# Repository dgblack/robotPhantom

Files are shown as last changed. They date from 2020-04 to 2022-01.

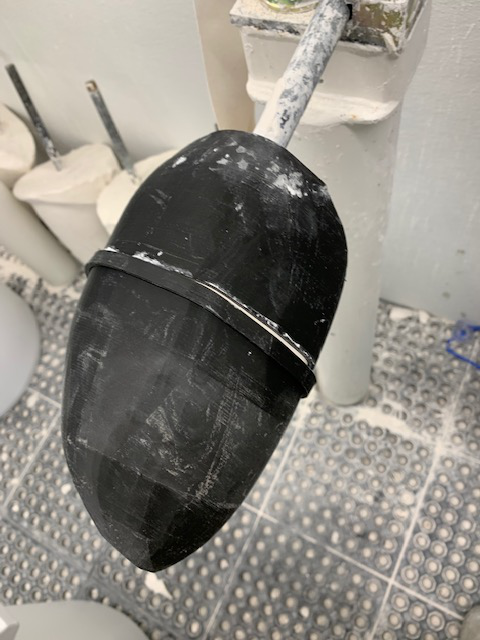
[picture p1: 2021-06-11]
Photos:Videos/image01.jpeg

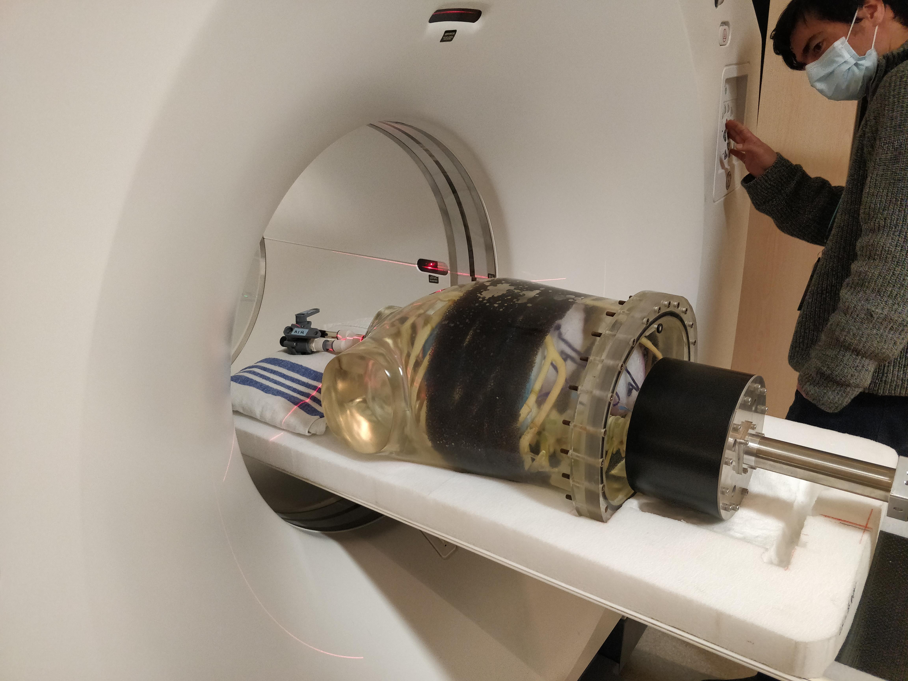
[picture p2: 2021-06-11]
Photos:Videos/IMG_20210426_1102451.jpg

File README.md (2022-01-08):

# Robotic PET Phantom

### Authors:
- David Black  (Engineering Physics, University of British Columbia, Vancouver, Canada)
- Yas Oloumi Yazdi (Engineering Physics, University of British Columbia, Vancouver, Canada)
- Jeremy Wong (Engineering Physics, University of British Columbia, Vancouver, Canada)
- Ivan Klyuzhin (BC Cancer Research Centre, Vancouver, Canada)

### Overview:
Full mechanical, electrical, and software design of an anatomically realistic, anthropomorphic PET phantom with human-like breathing motion. The phantom is robust and can achieve fast breathing rates (over 25 breaths per minute) even at high tidal volumes (up to 1000mL). The lungs have not yet been fabricated due to the COVID-19 pandemic.

### Videos and Photos:
See demo video [here](https://youtu.be/zXkUx0RQXnE)  
Some videos and photos from testing [here](https://ubcca-my.sharepoint.com/:f:/g/personal/dgblack_student_ubc_ca/Ejtq5QNHxeNPp8weYnc7cZwBMOwxvVZQ7KxTPI8Fzo8WOQ)

### Paper:
To read about the phantom, read the Medical Physics paper about it [here](https://github.com/dgblack/robotPhantom/blob/3cfdd82dce6134d97d138fe47dd0202dabd2ce38/MedicalPhysicsPaper.pdf)\
See ePoster [here](https://w3.aapm.org/meetings/2020AM/programInfo/programAbs.php?sid=8796&aid=51718)

### User Manual:
For full details, documentation, user manual, click [here](https://github.com/dgblack/robotPhantom/blob/master/phantomUserManual.pdf)

### Bill Of Materials:
View the BOM [here](https://docs.google.com/spreadsheets/d/1NjVN7iGE2hLrNtNaS808veyB4rukoj4t-0Kp28Ju0Y0/edit?usp=sharing)\
Or download a PDF version [here](https://github.com/dgblack/robotPhantom/raw/master/BillOfMaterials.pdf)

### CAD Models 
(Plus machine shop drawings, DXF files for waterjetting, STL files for 3D printing)\
View files [here](https://github.com/dgblack/robotPhantom/tree/master/CAD)

### Software
Code is found [here](https://github.com/dgblack/robotPhantom/tree/master/src)

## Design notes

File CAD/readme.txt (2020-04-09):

The CAD files are named by part number, which can be referenced from the Bill Of Materials. Certain DXF files for waterjet cutting, drawings for machine shops, and STL files for 3D printing are included in the Fabrication folder. While these are easily reproduced by exporting from SolidWorks, they are the files we used for fabrication.

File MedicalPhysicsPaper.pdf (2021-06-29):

## Design of an anthropomorphic PET phantom with elastic lungs and respiration modeling

David G. Black, Yas Oloumi Yazdi and Jeremy Wong
Department of Physics and Astronomy, University of British Columbia, Vancouver, BC, Canada
Roberto Fedrigo
Department of Physics and Astronomy, University of British Columbia, Vancouver, BC, Canada BC Cancer Research Institute, Vancouver, BC, Canada
Carlos Uribe
Department of Functional Imaging, BC Cancer, Vancouver, BC, Canada
Department of Radiology, University of British Columbia, Vancouver, BC, Canada
Dan J. Kadrmas
Department of Radiology and Imaging Sciences, University of Utah, Salt Lake City, UT, USA
Arman Rahmima)
Department of Physics and Astronomy, University of British Columbia, Vancouver, BC, Canada BC Cancer Research Institute, Vancouver, BC, Canada
Department of Radiology, University of British Columbia, Vancouver, BC, Canada
Ivan S. Klyuzhin
BC Cancer Research Institute, Vancouver, BC, Canada
Department of Radiology, University of British Columbia, Vancouver, BC, Canada
(Received 27 December 2020; revised 6 May 2021; accepted for publication 10 May 2021; published xx xxxx xxxx)
Purpose: Respiratory motion during positron emission tomography (PET) scans can be a major detriment to image quality in oncological imaging. The impact of motion on lesion quantification and detectability can be assessed using phantoms with realistic anatomy representation and motion modeling. In this work, we develop an anthropomorphic phantom for PET imaging that combines anatomic fidelity and a realistic breathing mechanism with deformable lungs.
Methods: We start from a previously developed anatomically accurate but static phantom of a human torso, and add elastic lungs with a highly controllable actuation mechanism which replicates the physics of breathing. The space outside the lungs is filled with a radioactive water solution. To maintain anatomical accuracy and realistic gamma ray attenuation in the torso, all motion mechanisms and actuators are positioned outside of the phantom compartment. The actuation mechanism can produce custom respiratory waveforms with breathing rates up to 25 breaths per minute and tidal volumes up to 1200 mL. Results: Several tests were performed to validate the performance of the phantom assembly, in which the phantom was filled with water and given respiratory waveforms to execute. All parts demonstrated expected performance. Force requirements were not exceeded and no leaks were detected, although continued use of the phantom is required to evaluate wear. The motion of the lungs was determined to be within a reasonable realistic range.
Conclusions: The full mechanical design is described in this paper, as well as a software application with graphical user interface which was developed to plan and visualize respiratory patterns. Both are available online as open source files. The developed phantom will facilitate future work in evaluating the impact of respiratory motion on lesion quantification and detectability in clinical practice. © 2021 American Association of Physicists in Medicine [https://doi.org/10.1002/mp.14998]

Key words: anthropomorphic phantom, motion correction, motion management, pet, phantoms -physical, quantitative imaging/analysis

1. INTRODUCTION

Positron emission tomography (PET) imaging is widely used in oncology for tumor detection, monitoring, and quantification. A leading factor that can adversely affect the quality of thoracic PET images is respiratory motion during the scans.¹ In normal respiration, the amplitude of diaphragm movement is on the order of 1.5–2 cm,² while deep inspiration may result in 7–13 cm diaphragm displacement.³ For clinical PET scanners with spatial resolution around 0.4–0.5 cm fullwidth at half-maximum (FWHM), motion of this magnitude can lead to effective resolution closer to 1 cm.⁴,5 This can reduce contrast for small lesions (e.g. cancer metastases⁶ ),
worsen lesion detectability, and introduce bias in the measured standardized uptake values (SUVs). In some cases, the measured values of functional metrics such as mean and
1 | Med. Phys. 0 (0), xxxx | 0094-2405/xxxx/0(0)/1/xx | © 2021 American Association of Physicists in Medicine | 1

maximum SUV (SUVmean, SUVmax) can directly affect therapy planning and post-treatment outcome analysis.⁷,8 For larger lesions, respiratory motion may likewise introduce bias in radiomic features that quantify lesion shape and texture.⁹⁻ 11 Additionally, the mismatch between PET and computed tomography (CT) images due to motion may lead to errors in attenuation correction and scatter estimation.¹²,13
Hence, there is an extensive ongoing effort to understand and evaluate the effect of respiratory motion in routine clinical PET imaging, particularly with respect to thoracic lesion detectability and quantification.¹⁴⁻¹⁶ For a quantitative assessment of such effects, it is necessary to obtain the ground truth activity values of lesions without respiration. In human subjects, respiratory gating and/or breath hold techniques can be used to reduce the effects of respiratory motion to obtain in vivo proxy measures of ground truth lesion activities, but these techniques are imperfect, subject to increased noise, and may be challenging in practice.¹⁷ In contrast, physical phantoms with various levels of complexity and realism offer a powerful experimental approach where the ground truth activity is precisely known. One of the most common approaches is to mount a rigid torso phantom on an actuated platform that can generate translational motion with a precisely known trajectory, such as the QUASAR system (Modus QA, Ontario, Canada). For example, such an approach was used by Liu et al.,¹⁸ who reported underestimation of SUVmax by 28% for 1 cm lesions due to motion. In another study that used a similar approach, contrast recovery for hot spheres in a phantom was found to be reduced by nearly 50% due to motion.¹⁹ With continuing advances in PET scanner sensitivity and resolution,²⁰ as well as development of novel image quantification paradigms,²¹ it becomes of interest to evaluate the effects of respiratory motion under more anatomically realistic conditions. Rigidly moving thorax phantoms, no matter how geometrically realistic, do not simulate several important effects of respiratory motion, namely motion of organs and lesions with respect to the ribcage, or changes in attenuation due to lung volume change. In order to simulate such effects, relative movement of internal compartments inside the phantom must be implemented. The goal of this work was to develop an anthropomorphic phantom for PET imaging, which combines anatomic fidelity and a realistic breathing mechanism with deformable lungs. We propose and test an approach wherein elastic lungs are manufactured from 3D-printed molds, and actuation is performed by means of creating a negative pressure differential inside the thorax – similar to how real breathing occurs in humans. We build upon an existing phantom previously developed by Kadrmas et al.,²²,23 henceforth referred to as “Probe-IQ” (Image Quality Probe), which has previously been static and not used to study motion effects. To the best of our knowledge, Probe-IQ to this day has the highest level of anatomical realism in the field. In the development of the motion-enabled phantom and lung actuation mechanism described in this paper, we use the shell and rib-cage of the original Probe-IQ phantom, but add custom-built elastic lungs with trachea, and an electronically controlled linear actuator to drive the lung deformation. The phantom is intended for use in PET imaging to evaluate the effect of respiratory motion on lesion quantification.
Several other anthropomorphic phantoms with focus on respiratory motion modeling in PET/CT imaging have been developed in the past; they are listed in Table I in comparison to the motion-enabled Probe-IQ. While Wilhelm²⁴ has the most realistic overall motion of any existing device, it lacks any bone structure, which is important for accurately modeling the gamma ray attenuation and scatter. Conversely, Alderson²⁵ has bones as well as respiratory and cardiac motion; however, its anatomy is simplified and it does not support the addition of lesions. Besides PET/CT imaging, several anthropomorphic phantoms have been developed specifically for radiation dosimetry and radiotherapy planning.²⁶,27 In such phantoms lungs are typically inflated using a ventilator that applies positive air pressure.²⁸⁻³⁰ However, driving lungs by ventilation is difficult when they are surrounded by an incompressible medium, for example, a radioactive water solution. In contrast, our approach is based on a more realistic principle of creating a negative pressure differential inside the thorax, forcing the lungs to inflate; the advantages of this approach are described later in the manuscript.
In this paper, we carefully consider the technical challenges associated with the proposed phantom design, and describe the functional requirements. To facilitate the re-use of our work by other groups, the implementation of the phantom is described in detail, including open-sourced schematics, materials, and software. Finally, we test the function of the completed phantom assembly and perform CT scans with artificial lung lesion tracking to validate the proposed method of lung actuation.
2. MATERIALS AND METHODS
2.A. Design overview
The Probe-IQ phantom enhanced with respiratory motion capabilities aims to achieve the following:
- Anatomical accuracy
- Builds off the static anatomical accuracy of Probe-IQ and achieves realistic lung motion.
- Avoids any unrealistic parts like connecting rods or metal components in the torso.

TABLE I. Comparison of existing anthropomorphic phantoms of interest.

Name

PET/CT/
MRI CM RM LM SS Lesions

Probe-IQ + Respiratory
motion capabilities
| ✓/ ✓/ × | × | ✓ | ✓ | ✓ | ✓
Probe-IQ²²,23 | ✓/ ✓/ × | × | × | × | ✓ | ✓
Wilhelm²⁴ | ✓/ ✓/ ✓ | ✓ | ✓ | ✓ | × | ✓
Alderson²⁵ | ✓/ ✓/ × | ✓ | ✓ | × | ✓ | ×

CM, cardiac motion; RM, respiratory motion; LM, liver motion; SS, skeletal structure.

Medical Physics, 0 (0), xxxx

2 | Black et al.: Anthropomorphic respiratory PET phantom | 2

- All materials carefully selected with reference to mass attenuation coefficients³¹ or tests²⁴ to resemble human tissue.
- Respiratory motion control
- Able to achieve a wide range of breathing rates and tidal volumes (i.e. air displaced between inhalation and exhalation). Namely, at least up to 25 breaths per minute at 1 L tidal volume; typical relaxed breathing is 500 mL tidal volume at 15–20 breaths per minute.³²
- Has highly controllable, repeatable, consistent breathing motion to generate high quality data, but also can include occasional disrupted breaths or inconsistencies, as would happen in a real patient.
- Realistic actuation principle.

In addition, safety is a concern, as the phantom is filled with approximately 15 L of radioactive solution (300 to 1000 MBq of radioactivity per scan) for PET acquisitions. The design must avoid leaks, and minimize the possibility of large spills. Easy fill-ability of the phantom is also desirable to reduce radiation exposure to users and to increase usability.
The respiratory motion-enabled Probe-IQ phantom involves three main components: (a) elastic and realistically shaped lungs, (b) an actuation method, and (c) a control system (electronics and software). The overall structure can be seen in Fig. 1 and all design files and code can be accessed in the Open Source Section at the end of this paper. The lungs are located inside the rib cage of the existing Probe-IQ phantom (A), and surrounded by a radioactive water solution creating the nonspecific radioactivity background typically present in oncological PET images. The lungs are connected to the atmosphere by a breathing tube (trachea) (F), which can be sealed at the neck. The actuating mechanism is positioned below the phantom (B, C, D), where the pelvis of a human would be located. It is outside the field of view of the PET scanner with a standard axial extent, so as not to create image artifacts. The phantom operates by piston-actuated passive breathing, as explained below and seen in Fig. 2.
To achieve respiratory motion with the lungs, the mechanism modulates the volume or pressure of the whole phantom in a manner analogous to real human breathing. Since the phantom is sealed, rigid, and entirely filled with water, except for the air-filled lungs, changing its volume by ΔV induces an equal volume change of ΔV in the lungs. Instead of compressing the air in a sealed set of lungs, the pressure requirement of the actuating mechanism can be dramatically decreased by opening the lungs to the atmosphere once the phantom has been filled and sealed. Contrary with intuition, the lungs do not collapse under the pressure of the water since the water volume is constant and cannot expand to fill the vacant space created if the lungs were to collapse. In effect, a relative negative pressure is created in the liquid anterior to the lungs, just as human breathing relies on negative intrapleural pressure. Now, when the volume of the torso is changed, that volume of air is simply exhaled to or inhaled from the atmosphere (Fig. 2).
To prepare the phantom for imaging, the lungs, organs, and bones are positioned inside the thorax, and the lungs are pressurized using a Schrader valve (Fig. 3) before completely filling the phantom with radioactive water solution. A valve in the base plate, at the highest point in the torso, is used to release the displaced air (Fig. 3). Once the phantom is filled and sealed, the lungs are opened to the atmosphere.
With the phantom setup, the user can define custom respiratory patterns, rates, and volumes using a graphical user interface. The piston then moves along the defined trajectory for the duration of a scan, causing the lungs to expand and contract. The next three sections describe the lungs, breathing mechanism, and software in more detail.

2.B. Lungs
The lung shapes were derived from a CT scan of an adult male and simplified using mesh editing software (Blender Foundation, Amsterdam) to reduce the cardiac notch and

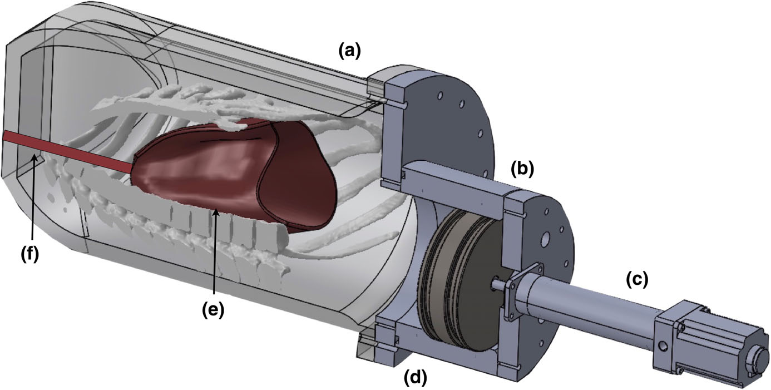
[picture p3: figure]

FIG. 1. Overview of phantom design. A: existing thorax shell and bone structure (liver and heart compartments included but not pictured). B: Piston and cylinder for torso volume modulation. C: linear actuator. D: custom-designed base-plate allows compatibility with existing Probe-IQ phantom. E: flexible lung inserts of silicone elastomer. F: breathing tubes (trachea) connect lungs to atmosphere to allow air transfer during inhalation and exhalation.

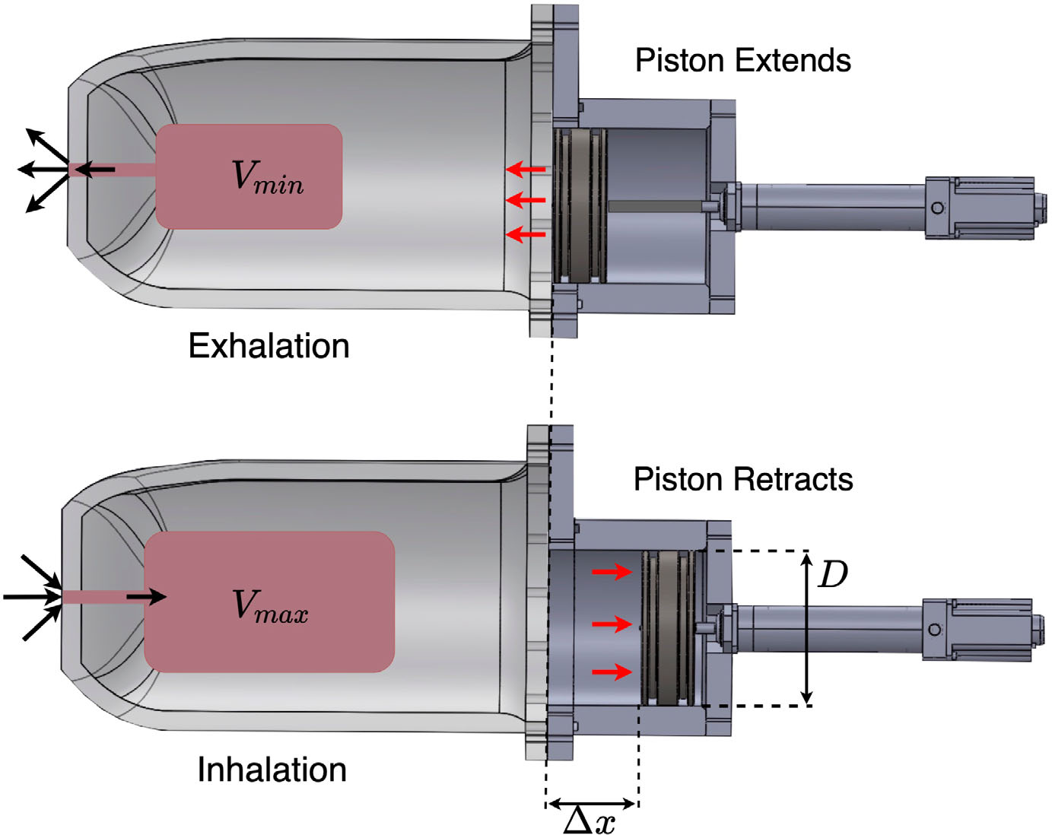
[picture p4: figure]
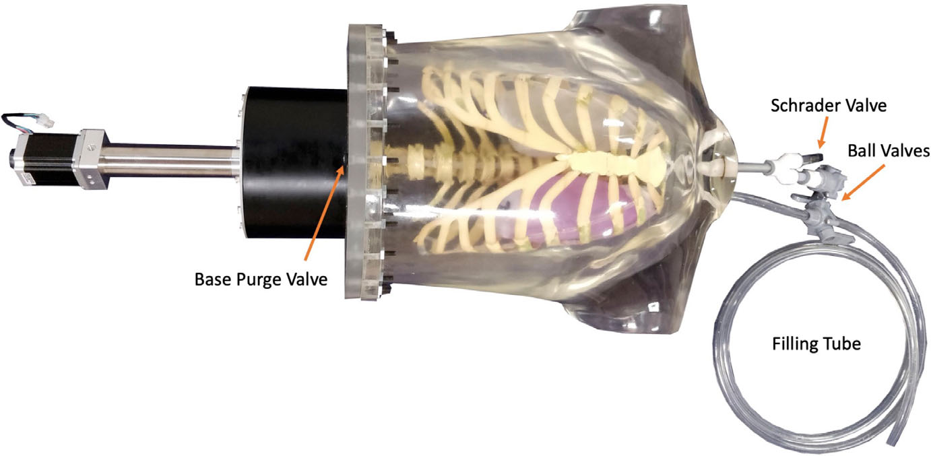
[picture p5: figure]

make the right and left lungs more symmetrical [Fig. 4(a)]. This was done primarily for ease of fabrication, but also to avoid unpredictable expansion and contraction of complex shapes which differ between the lungs. The lungs were designed to have a realistic adult size postexhalation, with a volume of 1650 ml each. This ensures that during normal breathing the lungs only expand, and do not compress or fold in an irregular manner. The dimensions of the lungs are approximately 18.0 cm (height) by 10.0 cm (width) by 12.7 cm (depth). The lungs have uniform wall thickness of 2 mm and can optionally be coupled directly to the piston using thin cables (not visible on reconstructed PET images) to force a specific longitudinal flex pattern.
A thru-wall fitting commonly used in prosthetics was custom manufactured using Delrin plastic [Fig. 4(b)]. This is attached medially near the top points of both lungs to connect air tubes which lead through a Y-connector to a single tube to the outside of the phantom, much like bronchi connecting to the trachea. One of three ports in the neck area of the phantom provides the inlet for the breathing tubes. The lungs are held in place in the superior/inferior axis using the trachea, and in the lateral and anterior/posterior axes using the rib cage. At the inlet of the trachea, near the neck of the phantom, another Y-connector splits the airway into a large ball valve and a Schrader valve which are used to alternatively pressurize and seal the lungs or allow free airflow (Fig. 3). The lungs were manufactured by rolling Chlorosil-35 (Ottobock, Germany), a silicone-based elastomer, onto a dental plaster lung model which was cast inside a 3D-printed negative mold. Following high temperature vulcanization, the

FIG. 2. Respiration modeling by modulating the volume of the phantom, mediated by incompressible fluid. Air flows into and out of the lungs through the trachea as the piston extends and retracts.

FIG. 3. Assembled phantom with filling system.

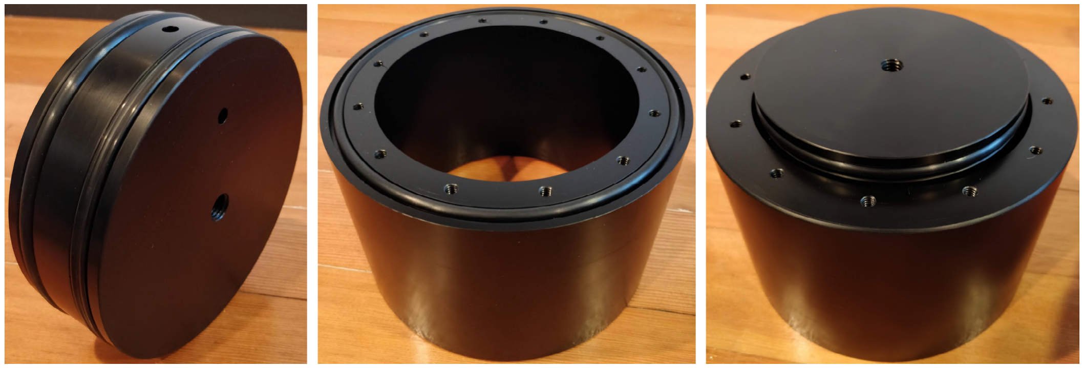
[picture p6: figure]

silicone material is durable, long-lasting, and thermostable, yet flexible to allow contraction and expansion. The material was previously tested in another phantom.¹⁰ A thin piece of stiffer plastic with a mounting point for a cable was placed in a silicone pocket at the base of each lung. To hold artificial lesions near the wall of the lungs, small silicone pockets can be added before vulcanization, or after, using silicone adhesive. A further method for holding lesions outside the lungs is to place them in slots cut into low-water/air resistance foam placed within the phantom compartments as previously described with the Probe-IQ phantom.²²,23
To hold artificial lesions inside the lungs for our motion validation experiments, the lungs were filled with soft foam cubes (uncompressed size 3–4 cm). Upon lung expansion, the foam cubes expand to fill the empty space, while helping maintain a constant relative lesion location [Fig. 4(c)]. Each lung was filled with 78 grams of foam (Active Foam Products, Inc., series DF1200 super soft, firmness 10) and contained three spherical lesions made from an epoxy resin (diameter 5–7 mm). The lesions were inserted into foam cubes and positioned in three different locations in the right and left lung respectively.

2.C. Breathing mechanism
To modulate the volume, both a rubber “diaphragm” membrane stretched across the entire phantom base and a piston mechanism were considered. After preliminary testing, the diaphragm mechanism was found to be unreliable, so the piston mechanism was chosen. This consists of a large cylinder attached directly to the base plate of the phantom. A piston is driven back and forth in the cylinder using a linear actuator to create the

(a)

(b)

(c)

Foam cubes
with embedded
lesions

Empty
foam
cubes

FIG. 4. (a) Lungs with bronchi and trachea. Bottom loops can be used to couple the lung motion directly to the piston if desired. Both lungs are the same material with different dyes. (b) Original (left) and custom manufactured plastic (right) thru-wall fitting (ESP LLC, New Jersey, USA) used to attach trachea to the lungs. The lung silicone is compressed between the twin flanges and creates an air-tight seal. (c) To hold artificial lesions in custom locations, the lungs were filled through the air opening with compressed foam cubes, some of which had lesions embedded (marked with red color).

FIG. 5. Left: Piston with dual O-rings; Center: Cylinder with O-ring to seal against base plate; Right: Piston in Cylinder. Threaded blind hole in piston to couple lung motion is visible.

volume change. The actuator works against the piston friction, water viscosity and inertia, and elastic forces in the lungs.
The mechanism consists of three major components: the piston and cylinder (Fig. 5), the base and mounting plates, and the linear actuator. Each is described below, before outlining their cumulative capabilities. The assembled mechanism is shown in Fig. 7.

2.C.1. Piston and cylinder
To achieve and maintain the tight tolerances (e.g. !0.1 mm over a 14 cm diameter) required to form a seal, while avoiding attenuation and scatter from metallic components, both the piston and cylinder were manufactured from Delrin acetal plastic. Delrin is dimensionally stable and machinable, has low water absorption, and a low friction coefficient of 0.2, which reduces the required actuator load.³³ The cylinder has 27 mm-thick walls to avoid warping, and a chamfer at the mouth of the cylinder ensures easy insertion of the piston without scratching the surfaces important for the seal.
Two opposing factors played a role in determining the inner diameter of the cylinder. The larger the diameter, the smaller the piston displacement must be for a given volume change, and thus the lower the speed requirement on the linear actuator. However, a larger piston is harder to machine within tolerance and to fit onto the base plate. A diameter of 14 cm was chosen as a compromise. At this diameter, the piston displacement for a given volume change is approximately equal to the axial lung extension for a given tidal volume in humans.³ For example, a piston movement of 3 cm leads to a volume change of 500 ml, which is a typical relaxed adult tidal volume. According to Wade et al.,³ the lungs should very roughly extend on average 1.5 cm for 500 ml tidal volume, though this varies widely between individuals. The system’s stroke is 8 cm, so with the chosen dimensions, tidal volumes of up to 1232 ml are possible, which constitute realistic deep breaths.
The piston has two O-ring grooves which ensure alignment inside the cylinder and provide a watertight dynamic seal (Fig. 6). The cylinder’s inner surface was honed to 8–16 μ in RA roughness to minimize wear and friction, and to improve the seal. A size −429 Buna-N rubber O-ring was selected for the same reasons, as well as its radiation resistance and large contact area for effective sealing. The cylinder is screwed to the base plate with an O-ring, and the actuator mounting plate screws into the backside of the cylinder. The flanged actuator is mounted directly to this plate. In this way, misalignment is minimized, and the whole structure is modular and easy to assemble and disassemble. The linear actuator screws directly into the piston, leaving minimal clearance between piston and mounting plate to maximize the positional range of the piston. The opposite side of the piston has an attachment point into which a cable to the lungs can optionally be fastened, or a rod can be attached to move an internal diaphragm. This gives flexibility in mounting and motion options.

2.C.2. Mounting plates
Two plates were made to mount the respiration mechanism to the existing Probe-IQ phantom, and to attach the linear actuator to the cylinder assembly. The former was fabricated from polycarbonate to avoid backscatter that could be caused by metal. Its dimensions were extracted from a CT scan of the phantom. A large, central hole was included for the piston, as well as 36 holes for mounting the cylinder to the base plate and the base plate to the phantom base flange in a secure, sealed manner with the load distributed evenly. Finally, a sealable hole was drilled into the plate at the highest point of the torso cavity to purge air.
As the second plate is further away from the scanner’s gantry and supported fully by the cylinder, it was fabricated from 3 mm-thick, waterjet-cut aluminum. The actuator mounts directly to the plate via a flange to minimize misalignment. This plate seals in any small leaks that potentially make it through the piston O-rings.

2.C.3. Linear actuator
The actuator type and model were selected based on the criteria outlined in Table II, as well as cost.
We set out to achieve a 1000 ml tidal volume at 25 breaths per minute. While the piston was designed to provide up to 1232 ml tidal volume, and the 90 mm actuator stroke supports the full range of piston motion, a linear speed of 54 mm/s is required to reach 25 breaths per minute at this amplitude (assuming the actuator accelerates instantly, which is reasonable since the chosen actuator has a maximum acceleration of 1667 mm/s²
). The required force is approximately the sum of the piston friction (Ff), the water inertia (Fi), and the elastic stretching of the lungs (Fe):

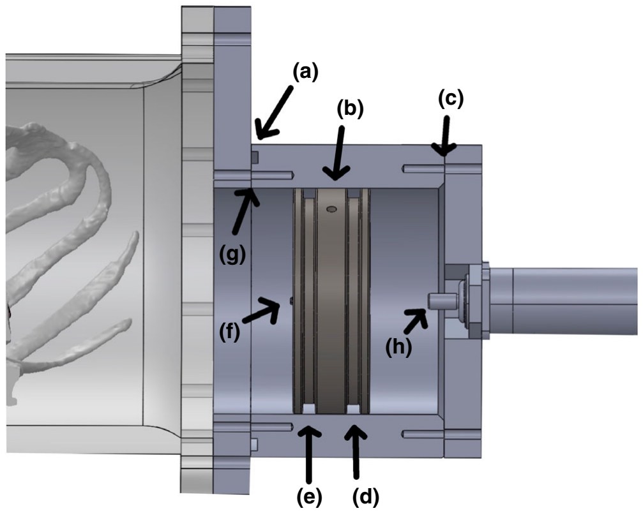
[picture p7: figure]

FIG. 6. Cross-section of the piston drive mechanism. A: Cylinder face O-ring groove. B: Inter-O-ring vent hole. C: Actuator mounting plate screw holes. D: Backup O-ring groove. E: Main O-ring groove. F: Insert for mounting piston-lung motion-coupling cable. G: Cylinder to base plate mounting screw holes. H: The linear actuator screws directly into the piston (see H in Fig), leaving minimal clearance between the piston and the actuator mounting plate to maximize the stroke length of the piston.

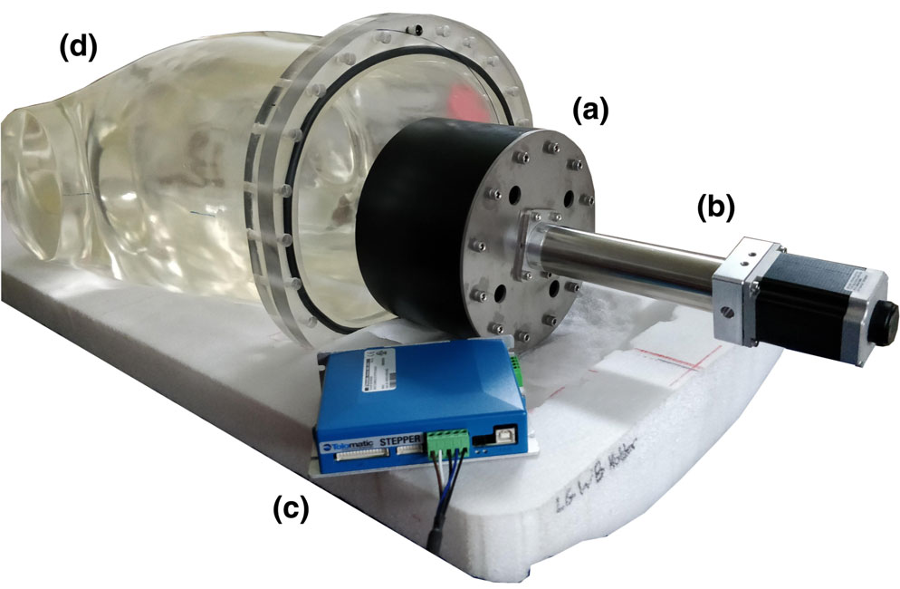
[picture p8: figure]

F ¼ Ff þFi þFe | (1)
Using the Parker O-Ring Handbook, the friction is approximately Ff = 250 N. To calculate the inertial force, assume the actuator accelerates to the 54 mm/s velocity within 0.5 cm, which constitutes an acceleration of a = 0.292 m/s²
. As a very conservative estimate, suppose all 17.3 kg of water in the phantom accelerate at this rate. Then:
Fi ¼ ð | Þ 17:3kg 0:292m=s
2 !" ¼ 5N | (2)

This is negligible compared to the frictional force. Similarly, the static pressure on the piston can be ignored because the water pressure on the front of the piston and the air pressure on the back cancel out.
To find the force required to stretch the lungs, assume that the lungs are cylindrical, and use the thin-wall approximation to find the hoop stress in one lung. This, however, also assumes that Hooke’s Law holds for rubber-like elastomers. Merrit and Weinhaus³⁴ found that this is not the case, and that after an initial linear section, the required pressure to increase the radius sharply falls off. Thus, Hooke’s Law provides an overestimate for large extensions. Let ‘, r, t be the cylindrical lung’s length, radius, and wall thickness, respectively, and ‘0 = 200 mm, r0 = 52 mm, and t0 = 2 mm be the initial values. These give the expected initial volume of 1700 ml, as well as an initial material volume of V 0

mat ≈ 2πr0t0(‘0 + r0) = 21000 mm³ .
Rubber is incompressible, so V 0

mat = V f

mat. Thus:
t≈ 2100
rðÞ ‘þr | (3)

Now using hoop stress, σH ¼ rΔp
t , and Hooke’s Law,
σH ¼ t0&t
t0 E, we obtain an expression for the required force applied by the piston:
Fe ¼ ðÞ 0:14 2 π
4

2100

r²ðÞ ‘þr 1& 2100
rt0ðÞ ‘þr

# $E:

The elastic modulus, E, of silicone rubbers can be estimated roughly from the Shore A durometer using Ruess’ Equation: log10 E = 0.0235S - 0.6403.³⁵ Since the lung silicone has Shore A hardness 35, E ≈ 1.5 MPa. Thus, to achieve a 1000 ml volume increase and about 6.6 cm lung extension,⁷ we take ‘ = 266 mm and r = 56.8 mm. Then Fe = 199 N.

Thus, according to Eq. (1), a conservative estimate for the maximum force required from the actuator is F = 450 N. Applying a factor of safety of 2, considering that these calculations were approximate, piston friction could increase with wear, and foam around the lungs could increase the pressure requirement, the linear actuator should be able to supply around 900 N of force.
To move the piston, a lead-screw actuation mechanism is preferred because of its superior controllability over pneumatic cylinders and other types of linear actuators. The phantom has to move continuously for the duration of the scan, which can be around 30 min, so the duty cycle has to be 100% for extended periods of time. A ball screw mechanism, which has much less friction than ACME lead screws, allows for continuous use and a long lifetime.
Based on these criteria, an ERD15 (Tolomatic, USA) ball-screw linear actuator was chosen, along with a stepper motor with encoder feedback. This relatively low-cost actuator is designed to run continuously and fulfills the load, stroke, and speed requirements. Assuming we carried out 30 min scans at the calculated force, at 25 breaths per minute and 1000 ml tidal volume, the actuator would have an estimated life of 5200 scans (according to manufacturer specifications³⁶). The ERD’s low profile and simplicity allow it to be mounted as seen in Fig. 7. The actuator position is accurate to within 0.03 mm per cm of movement.²³ Together with the 1.8 ˚/step stepper motor and 2000-count encoder feedback, this facilitates exact velocity and acceleration control.
The force analysis was verified during testing by running the actuator at 40% force, where it stalled, and then at 60%, where it ran smoothly. This implies that the required force is around 50% of the actuator’s force capability, which, given the chosen safety factor of 2, means the required force corresponds closely to the derived value.

2.D. Software and electrical design
The Tolomatic ERD15 actuator is driven by a stepper motor with encoder feedback, which is controlled by stepper

TABLE II. Linear actuator design requirements.

Criterion | Desired | Chosen actuator
Speed | 54 mm/s | 167 mm/s
Stroke | 90 mm | 90 mm
Force | 900 N | 890 N
Duty Cycle | 100% | 100%
Durability | High | 5200-scan estimated life
Controllability | High | See in text
Weight | Low | ≈1.5 kg

FIG. 7. Assembled breathing mechanism (A. cylinder containing piston, B. linear actuator, and C. stepper motor control box) with empty phantom (D).

driver hardware from Tolomatic. The goal in this control system is to create realistic, consistent, repeatable lung motion with flexibility in breathing rate and amplitude, as well as the ability to include breathing inconsistencies for added realism. Two distinct control methods were created for the phantom and are described below. The first is simple and fast to setup while the second provides more realism, so each is useful in different applications.
First, a free Windows application (described below) can be used to communicate with the stepper driver over USB to configure the actuator. The second option is analog position control. Here, a 0–10 V analog signal can be input to the driver, which moves to the corresponding position. Control through ethernet and Modbus RTU over RS-485 are also possible, but neither was investigated in this work.

2.D.1. USB interface
The actuator manufacturer provides a software interface called Tolomatic Motion Interface (TMI) to communicate with its stepper controllers over USB. While the software is primarily used to configure the driver initially, it can also be used to control the actuator’s motion directly. Moves can be defined with a certain acceleration, deceleration, velocity, and goal position. These moves can then be combined in any order to form a repeating series of up to 16 moves. Taking the simplest example, one may define just 2 moves, one to 45 mm, and one to 1 mm, and cycle between these two positions indefinitely. By combining more positions, however, and altering their accelerations and decelerations, a wide variety of motion patterns can be achieved, including realistic respiratory cycles.
The problem with this method is that it is difficult to visualize what the respiratory cycle will look like based on a series of linear position, velocity, and acceleration values. A graphical user interface (GUI) was therefore developed in Python to allow motion planning and visualization of the lung volume as a function of time (Fig. 8).
In the application, the user can define the breathing rate, amplitude, and base lung volume. We used published models²⁴ to identify a physiologically representative equation for a respiratory curve [Eq. (4); x = amplitude, t = time], which can be scaled and shifted to match the desired, user-defined breathing parameters. This curve is plotted in green in Fig. 8.
x ¼ e&1:71668t 0:0106þ2:3313t þ0:535t

2 þ3:959t

3
2:3062þ0:3517t &0:6487t² þ0:1177t³ (4)

The user can then define up to four moves with position, velocity, acceleration, and deceleration, and place them in any order. The corresponding motion profile is generated through iterative kinematic simulation of the actuator, and plotted in real time, in red in Fig. 8, as the parameters are changed. With the red actuator plot overlaid onto the green desired plot, the optimal set of motion parameters can be determined. It is also possible to save configurations in automatically formatted JSON files to be loaded later.

This control method is simple because the respiratory cycle is visualized, input into user-friendly software, and relayed to the actuator directly over USB. While a variety of motions can be achieved in this manner, it is nonetheless limited by the discrete nature of a set of individual moves. To overcome this problem, at the cost of simplicity, analog control can be used.

2.D.2. Analog position control
The second method controls the ERD15 actuator using a 0–10 V analog signal. The voltage range is mapped onto the positional range of the actuator so that a given voltage causes the actuator to move to that position. Thus, arbitrary continuous waveforms can be realized by the actuator, if they do not exceed the configured acceleration and velocity values. Figure 9 shows the setup used to generate the analog signal. The voltage was provided by an MCP4725 Digital to Analog Converter (DAC), controlled via the I2C GPIO pins of a Raspberry Pi microcomputer. The encoder feedback is read by the Raspberry Pi, and any control software is run on the Raspberry Pi.
For the actuator to respond to the analog input voltage, analog control must be enabled through a digital input. Thus, digital COM is tied to the power supply ground, and a voltage divider is used to provide the 24 V needed to enable motion. An N-channel MOSFET whose gate voltage is set by the Raspberry Pi switches the enable input between 0 and 24 V. With this setup, arbitrary waveforms can be saved as CSV files on the Raspberry Pi. A Python program converts the volumetric data to actuator positional curves using the piston geometry, and then to voltages using the voltage-position mapping. The voltages are sent via I2C to the DAC, where they are converted to analog voltages and input into the actuator, thus generating the desired lung motion.
3. RESULTS: TESTING AND VALIDATION
To validate the efficacy of the proposed phantom design, testing of the complete assembly was performed. The primary criteria for evaluation were realism in the trajectory, symmetry between the lungs, consistency of movement, and controllability, as well as validation of the force requirements and mechanical integrity. Two sets of experiments were performed, with optical tracking of continuous lung motion and CT scans acquired with a “step-and-shoot” technique.

3.A. Optical tracking experiments
The phantom was setup in the single O-ring configuration and was filled with water. Filling was performed using the neck ports. The lungs maintained their position and shape when opened to the atmosphere, and the piston was then run back and forth continuously for 30 min with cameras mounted above and on either side of the phantom. No water leakage to the outside of the phantom was observed. The piston was first set to move at 30 mm/s and then 40 mm/s, both

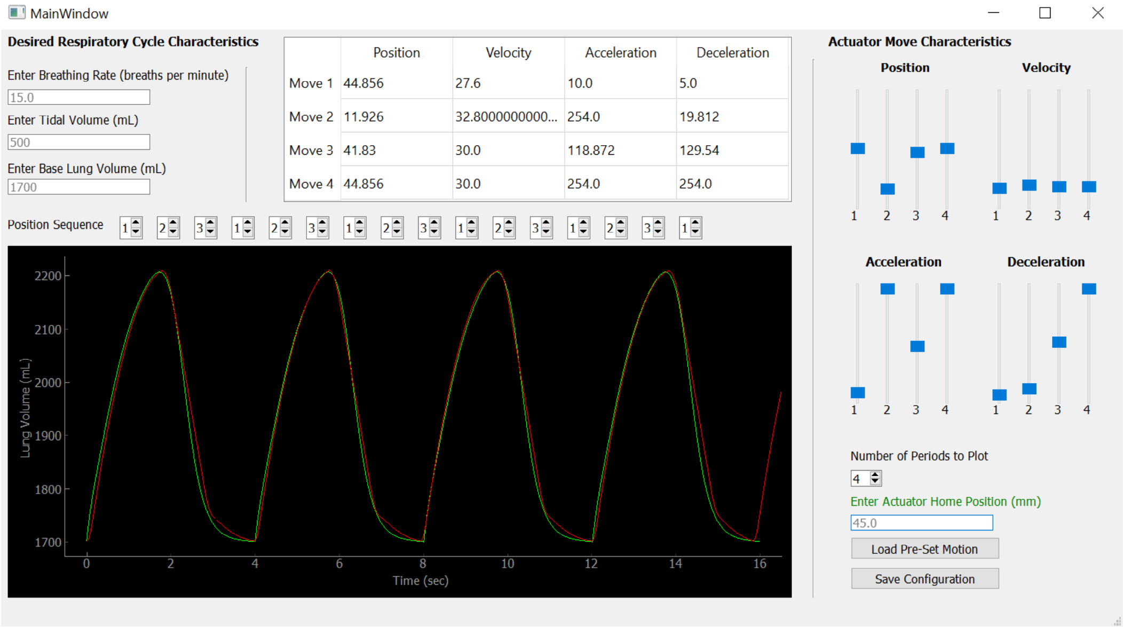
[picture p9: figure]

with a 58 mm amplitude. This corresponds to 892 ml tidal volume at 15 and 21 breaths per minute, respectively.
The resultant trajectory is shown in Fig. 10. The videos are available in the open source materials. Qualitatively, the breathing looked realistic, and included some rib motion and flexing, which adds to the realism. The lungs’ maximum and minimum positions were ascertained from the videos at all angles. There is little difference between the right and left lung, as seen when viewed from above (Fig. 10, right image).
Analysis of the actual displacements allows comparison to the average trajectories previously determined for adult males. The results are given in Table III, in comparison with previously published values.³ These results show that the lungs naturally expand slightly more in circumference and extend less axially than desired. However, they are within the reasonable realistic adult male range given by Wade’s measurements and his observation of variability between individuals.
Finally, the consistency of the motion was analyzed by tracking three markers placed on the left lung for 20 breaths. The frames were binned using the known frame rate of the video and the set breathing rate such that only frames showing the lungs at 100%, 75%, 50%, 25%, and 0% inhalation were used. The motion of each point formed a scatter plot through which a line was fitted, and the root-mean-squared (RMS) error was calculated as an indicator of the motion’s consistency. The resulting RMS errors were 0.74, 0.52, and 0.54 mm from the straight line. Note that the tracking error in the position measurements was about !1 mm, so the results show that the lung motion was consistent between the breaths.
After one test that included a total of 40 min of almost continuous motion, the phantom was emptied, and the drive mechanism was dismantled and inspected. There were no signs of wear in the mechanism, which would have indicated a problem. The O-ring remained very well lubricated, and the cylinder wall behind the O-ring was dry. It is expected that with continued good lubrication the chance of leakage will remain very low. Since the phantom rests on an absorbent sheet throughout operation and is left in isolation until the isotopes have decayed to background levels, individual drops that may get through the piston do not represent a concern, especially as they remain contained within the cylinder. However, the second O-ring can also be installed on the piston to further improve the seal.

3.B. CT scans of the phantom
To more precisely characterize the motion and deformation of foam-filled lungs with lesions, a series of seven CT scans corresponding to 0% to 100% inflation in equal intervals were carried out. Four images from the series are plotted in Fig. 11(top). At 0% inflation, a small amount of lung wall buckling can be seen, which can be resolved in future scans by increasing the internal lung air pressure during the phantom filling. Artificial lesion motion can be seen in the images, and the foam contributed to a more realistic texture inside the lungs,

FIG. 8. Screenshot of motion planning application. The green curve is the desired respiratory cycle, while the red is the pattern carried out by the phantom based on the GUI inputs.

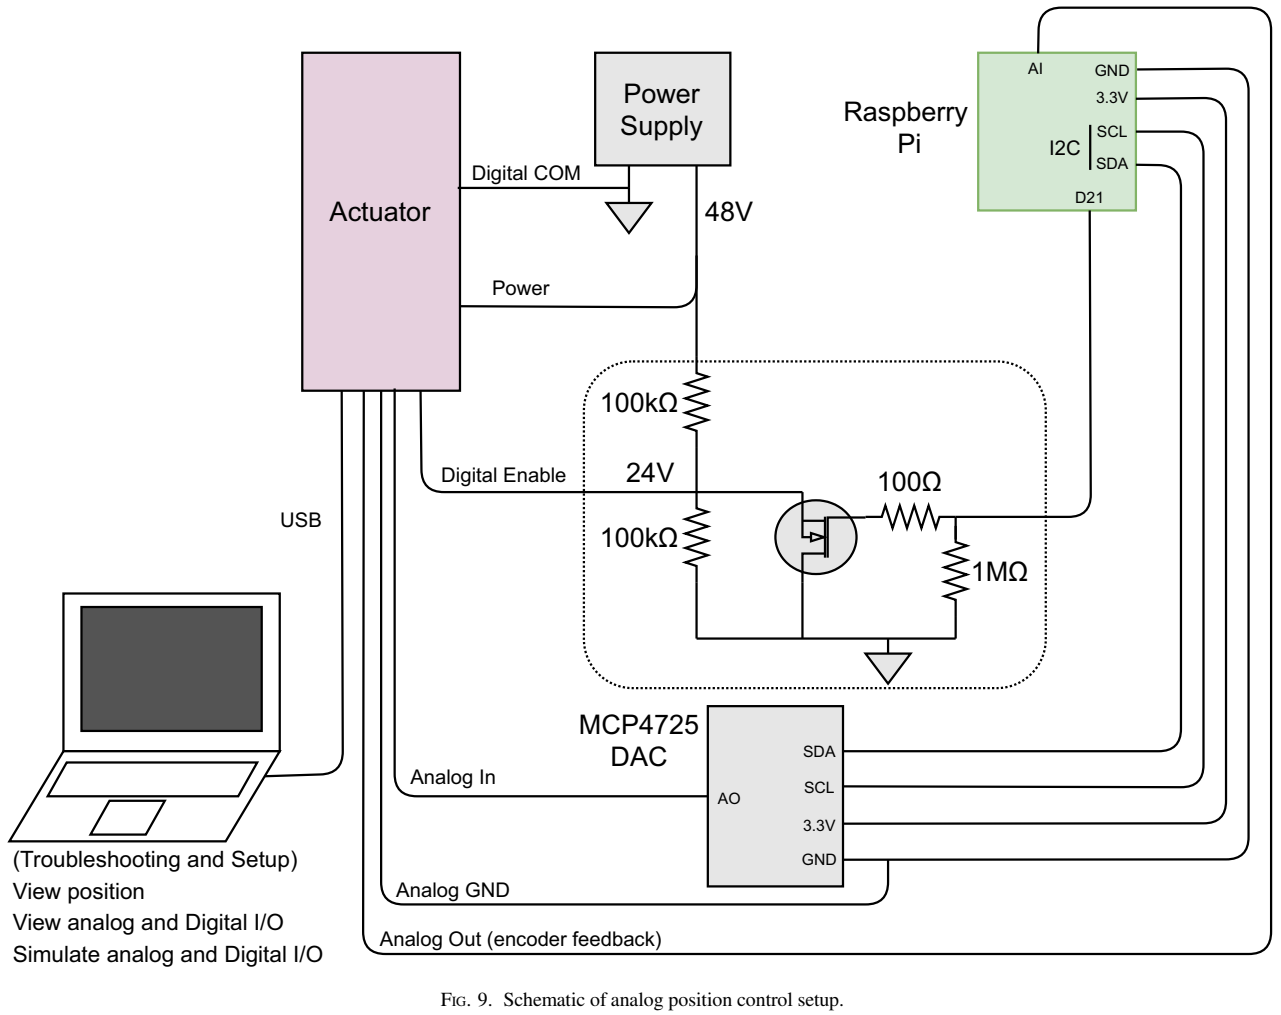
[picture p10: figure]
USB; Actuator; (Troubleshooting and Setup) View position View analog and Digital I/O Simulate analog and Digital I/O; Power Supply; GND 3.3V Raspberry; SCL; SDA; GND; MCP4725 DAC; Analog Out (encoder feedback); Analog In; Digital Enable; Power; Digital COM; Analog GND
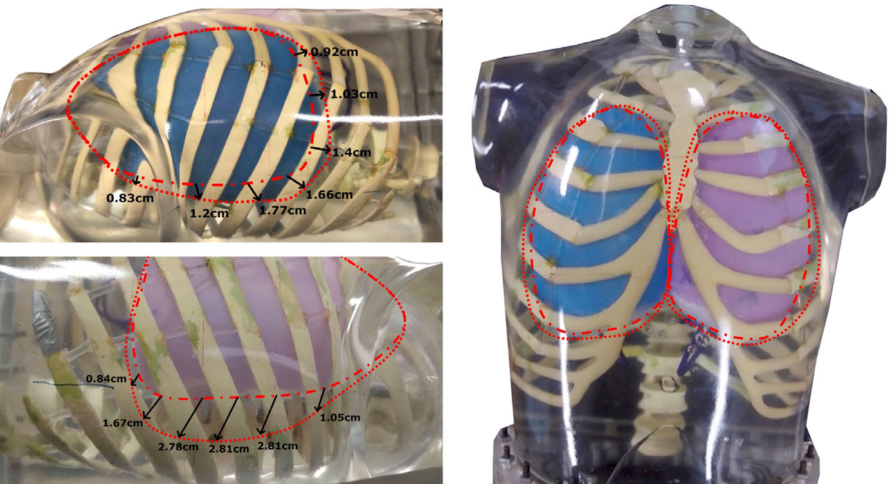
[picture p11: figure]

To characterize the consistency of relative lesion position inside the lungs during motion, CT scans were performed at 0%, 50%, and 100% inhalation for three sequential breathing cycles. The phantom was then set to breathe continuously for 150 cycles, and a further series of three scans was obtained to detect any shifts in the

FIG. 9. Schematic of analog position control setup.

FIG. 10. Screen grabs from the breathing test. The dotted lines indicate maximum inhalation, while the dashed lines indicate maximum exhalation. The tidal volume is 892 ml. Note that the camera angle on the right and left lungs are slightly different to show a different cross-section of the trajectory. The view of both lungs show that they move almost identically.

lesion position (i.e. 12 scans in total). The measured x, y, z coordinates of lesion centroids in the left and right lung are plotted in Fig. 11(bottom). The graphs demonstrate consistent lesion trajectories between sequential breathing cycles, as well as after 150 untracked cycles. The average standard error of the mean for 0%, 50%, and 100% inhalation was 0.23, 0.24, and 0.09 mm in the anterior– posterior, transverse, and axial coordinates, respectively, for all six lesions. Overall, the lungs moved in a controllable manner and it was found that the lesions did not shift out of position during respiration. A small drift of ~2 mm was found with the posterior lesion in the left lung. The respiration kinetics were realistic, with 920 ml tidal volume and 10–20 breaths per minute tested. Further videos and CT data can be found on the open source link below.

TABLE III. Lung trajectory comparison.

Parameter | Wade et al.³ | Phantom | Scaled
Tidal Volume | 799 ! 210 ml | 892 ml | 799 ml
Axial Extension | 1.7 ! 0.26 cm | 1.4 cm | 1.3 cm
Circumference Increase | 6.8 ! 2.2 cm | 8.4 cm | 7.5 cm

The “scaled” column is the measured parameters normalized to match Wade’s tidal volume for ease of comparison (assuming the parameters scale approximately linearly with volume in this range)

-200

0

200

400

600

800

1000

1200

1400

HU

0 | 1.0
2 | 4 | 6 | 8 | 10 | 12
Scan number

Lung inflation (x100%)

Scan/step number | Scan/step number
Scan/step number | Scan/step number | Scan/step number

290

300

310

320

330

340

350

X-Coordinate of Lesion

Left Lung

2 | 4 | 6 | 8 | 10 | 12 170

180

190

200

210

220

230

X-Coordinate of Lesion

Right Lung

2 | 4 | 6 | 8 | 10 | 12 160

180

200

220

240

260

280

300

Y-Coordinate of Lesion

2 | 4 | 6 | 8 | 10 | 12 180

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
Y-Coordinate of Lesion

2 | 4 | 6 | 8 | 10 | 12 160

165

170

175

180

185

Z-Coordinate of Lesion

2 | 4 | 6 | 8 | 10 | 12 160

170

180

190

200

210

Z-Coordinate of Lesion

Base Lesion Anterior Lesion Posterior Lesion

Base Lesion Anterior Lesion Posterior Lesion

150 breathing cycles

150 breathing cycles

150 breathing cycles

150 breathing cycles

150 breathing cycles
150 breathing cycles

0.5 1.0 0 0.5 1.0 0 0.5 1.0 0 0.5

0 | 1.0

Lung inflation (x100%)
0.5 1.0 0 0.5 1.0 0 0.5 1.0 0 0.5 | 1.0 0

Lung inflation (x100%)
0.5 1.0 0 0.5 1.0 0 0.5 1.0 0 0.5 | 1.0 0

Lung inflation (x100%)
0.5 1.0 0 0.5 1.0 0 0.5 1.0 0 0.5
0 | 1.0

Lung inflation (x100%)
0.5 1.0 0 0.5 1.0 0 0.5 1.0 0 0.5 | 1.0 0

Lung inflation (x100%)
0.5 1.0 0 0.5 1.0 0 0.5 1.0 0 0.5
0% | 33.3% | 66.6% | 100% | 0% - 100% difference

FIG. 11. (Top) Coronal and transverse planes of CT scans of the phantom corresponding to 0%, 33.3%, 66.6%, and 100% lung inflation, and the difference image between 0% and 100% inflation. Yellow markers are added for reference, and blue arrows indicate artificial lesions. (Bottom) X (anterior-posterior), Y (leftright), and Z (inferior-superior) coordinates of the three lesions in the left and right lungs, measured at 0%, 50%, and 100% inhalation for three successive breaths, followed by a fourth series of measurements after 150 cycles. All lesions show small deviations from their mean positions (dashed lines).

4. DISCUSSION
We have developed and validated the main aspects of the phantom design and usability, including materials, fabrication, couplings, actuation, dynamics, control, and procedures, such as filling the phantom. These elements have been shown to work together well to achieve the desired purpose of modeling nonrigid lung motion inside an anthropomorphic phantom. The design objectives of consistent, controllable, symmetric, and realistic motion have been met, although there are a few aspects that can be improved in future iterations.
In normal respiration, lungs typically expand more axially than cross-sectionally.⁷ In the developed phantom, the lung expansion was more uniform. Thus, artificial lesions attached to inferior lobes of the manufactured lungs travel a shorter path on average compared to reality (for a similarly-sized person). Two approaches can be taken to increase the axial expansion. First, the lungs could be coupled directly to the piston using an elastic cord. Making this coupling looser or tighter would produce more or less axial extension, while also keeping the lungs centered in the antero-posterior direction. Alternatively, during the lung fabrication the wall material (Chlorosil) can be strategically rolled thinner in parts that should expand more.
In addition, though the ribs flex to accommodate the lung expansion, the torso shell is rigid, so the lungs are forced to expand dorsally instead of the chest rising as it does in humans. However, by attaching the lungs to the spine so they do not float up when the phantom is placed in a supine position, they can expand upwards during inhalation. In this way, lesions placed on the lungs near the chest retain the expected, anatomically correct trajectory, though their motion relative to the ribs may differ slightly from that in patients.
A limitation of the current design is that with foam inside the lungs, the gamma attenuation coefficient of the lungs was approximately 15% of that for soft tissue, whereas in reality, it should be around 40%.²³ This could be addressed in the future by more carefully selecting the foam material, and possibly by adding water to the foam.
Foam can also be used to fill the space outside the lungs to introduce realistic image heterogeneity through small air bubbles caught in the foam and to facilitate organ placement (liver and heart), as shown previously in the Probe-IQ.²²,23 The foam could also potentially transmit the lung motion to the other organs, leading, for example, to liver motion, and lesions can be placed in arbitrary locations by cutting pockets into the foam. Here the foam’s effect on lung expansion, and the potential for all the bubbles to escape the foam under the constant motion must be assessed. To improve the realism of motion and deformation of other organs, they could also be manufactured using the same method as the lungs out of silicone elastomer.
By means of optical tracking and sequential CT scans, we found that the phantom motion was consistent between breaths. Since the actuator is very precise and can be programmed with the exact same motion, the movement is also expected to be consistent between different tests (i.e. scan repetitions). Any possible movement variations between tests would stem from changes in the initial lung axial position, rotation, and inflation. Positional changes are mitigated using foam around the ribs which ensures a similar setup every time,²³ and by marking a point on the trachea that aligns with a mark on the phantom neck port to ensure consistent alignment. A pressure gauge can be used to obtain consistent initial inflation of the lungs.
The described phantom design, materials, and principle of operation can facilitate the construction of similar phantoms elsewhere, and guide the development of a next iteration of phantoms for PET/CT imaging. For this purpose, we have documented and made available open-source every detail of the design. While the anthropomorphic shell, ribs, and organs for the Probe-IQ phantom are for the most part commercially available (Radiology Support Devices, Inc., Long Beach, CA), the focus of this work is the addition of lungs and a motion mechanism, which can be adapted to other phantoms. Indeed, the linear actuator is commercially available while the designs of all other components are available with fabrication instructions (see Open Source section).
Once COVID-19 restrictions at our center are eased, pilot PET scans will be performed to characterize the effect of lung motion on lesion quantification in a realistic environment. In future work, we will report the results of initial PET scans, compare the performance to previously created phantoms from literature, and investigate methods to further improve the realism of the lung motion.
5. CONCLUSION
In this work, we presented a method and mechanical design to incorporate anatomically accurate, elastic lungs and respiratory motion into an anthropomorphic phantom for PET/CT imaging. The proposed physical principle of operation, materials, couplings, and electronics have been validated. A new method to fabricate elastic lung models using 3D-printed molds was established and tested, and a software interface to plan and visualize these breathing patterns was developed, with two separate control schemes. The design can achieve a variety of respiratory wave-forms with up to 25 breaths per minute at 1232 ml tidal volume, and is expected to contribute to studies evaluating the effect of respiratory motion on detectability and quantification of cancer lesions.

OPEN SOURCE
To promote further development of PET/CT and phantom technology, we have open-sourced the entire design, including all CAD files, code, engineering drawings, and more, with supporting documentation. This material can be found here: https://github.com/dgblack/robotPhantom.

ACKNOWLEDGMENT

We gratefully acknowledge support by Daryl Murphy, David Moe, and Malena Rapaport at Barber Prosthetics

(Vancouver, Canada) in all aspects related to lung manufacturing. Robert de Rot at PQ Systems Ltd (Vancouver, Canada) provided guidance and a demo linear actuator for initial testing. Foam samples were provided by Discount Foam (Vancouver, Canada). This work was supported by the National Institutes of Health (NIH) / Canadian Institutes of Health Research (CIHR) Quantitative Imaging Network (QIN) Grant number 137993, and by BC Cancer Foundation. We also gratefully acknowledge the Engineering Physics Project Lab at the University of British Columbia for financial and expertise support.

CONFLICT OF INTEREST
The authors have no conflicts to disclose.

a)Author to whom correspondence should be addressed. Electronic mail: arman.rahmim@ubc.ca

REFERENCES

1. Valk PE, Abella-Columna E, Haseman MK, et al. Whole-body PET imaging with [18F]fluorodeoxyglucose in management of recurrent colorectal cancer. Arch Surg. 1999;134:503–511. http://www.ncbi.nlm.nih.gov/pubmed/10323422. (http://www.ncbi.nlm.nih.gov/pubmed/10323422)
2. Dawood M, Lang N, Jiang X, Schafers KP. Lung motion correction on ¨ respiratory gated 3-D PET/CT images. IEEE Trans Med Imaging. 2006;25:476–485.
3. Wade OL. Movements of the thoracic cage and diaphragm in respiration. J Physiol. 1954;124:193–212.
4. Nayyeri F. A review on motion correction methods in PET/CT images for detection of cancer cells. Acta Medica Bulg. 2015;42:68–78.
5. Schmitz R, Alessio A, Kinahan P. The Physics of PET/CT Scanners.
6. Nehmeh SA, Erdi YE, Ling CC, et al. Effect of respiratory gating on reducing lung motion artifacts in PET imaging of lung cancer. Med Phys. 2002;29:366–371.
7. Doot RK, McDonald ES, Mankoff DA. Role of PET quantitation in the monitoring of cancer response to treatment: review of approaches and human clinical trials. Clin Transl imaging. 2014;2:295–303.
8. Hayden AR, Tonseth P, Lee DG, et al. Outcome of primary mediastinal large B-cell lymphoma using R-CHOP: impact of a PET-adapted approach. Blood J Am Soc Hematol. 2020;136:2803–2811.
9. Guerra L, De Ponti E, Elisei F, et al. Respiratory gated PET/CT in a European multicentre retrospective study: added diagnostic value in detection and characterization of lung lesions. Eur J Nucl Med Mol Imaging. 2012;39:1381–1390.
10. Manber R, Thielemans K, Hutton B, et al. Clinical impact of respiratory motion correction in simultaneous PET/MR, using a joint PET/MR predictive motion model. J Nucl Med. 2019;59:1467–1493.
11. Rakvongthai Y, El Fakhri G. Magnetic resonance-based motion correction for quantitative PET in simultaneous PET-MR imaging. PET Clin. 2017;12:321–327.
12. Sureshbabu W, Mawlawi O. PET/CT imaging artifacts. J Nucl Med Technol. 2005;33:156–161.
13. Chi A, Nguyen N. 4D PET/CT as a strategy to reduce respiratory motion artifacts in FDG-PET/CT. Front Oncol. 2014;4:205.
14. Geramifar P, Zafarghandi MS, Ghafarian P, Rahmim A, Ay MR. Respiratory-induced errors in tumor quantification and delineation in CT attenuation-corrected PET images: effects of tumor size, tumor location, and respiratory trace: a simulation study using the 4D XCAT phantom. Mol Imaging Biol. 2013;15:655–665.
15. Siman W, Mawlawi OR, Mikell JK, Mourtada F, Kappadath SC. Effects of image noise, respiratory motion, and motion compensation on 3D activity quantification in count-limited PET images. Phys Med Biol. 2016;62:448.
16. Cui Y, Bowsher J, Cai J, Yin F-F. Impact of moving target on measurement accuracy in 3D and 4D PET imaging—a phantom study. Adv Radiat Oncol. 2017;2:94–100.
17. Kawano T, Ohtake E, Inoue T. Deep-inspiration breath-hold PET/CT of lung cancer: maximum standardized uptake value analysis of 108 patients. J Nucl Med. 2008;49:1223–1231.
18. Liu C, Pierce LA II, Alessio AM, Kinahan PE. The impact of respiratory motion on tumor quantification and delineation in static PET/CT imaging. Phys Med Biol. 2009;54:7345.
19. Walker MD, Bradley KM, McGowan DR. Evaluation of principal component analysis-based data-driven respiratory gating for positron emission tomography. Br J Radiol. 2018;91:20170793.
20. Zhang X, Xie Z, Berg E, et al. Total-body dynamic reconstruction and parametric imaging on the uEXPLORER. J Nucl Med. 2020;61:285– 291.
21. Gillies RJ, Kinahan PE, Hricak H. Radiomics: images are more than pictures, they are data. Radiology. 2016;278:563–577.
22. Kadrmas D, Casey M, Conti M, Jakoby B, Lois C, Townsend D. Impact of time-of-flight on PET tumor detection. J Nucl Med. 2009;50:1315–23.
23. Kadrmas D, Casey M, Black N, Hamill J, Panin V, Conti M. Experimental comparison of lesion detectability for four fully-3D PET reconstruction schemes. IEEE Trans Med Imaging. 2009;28:523–34.
24. Bolwin K, Czekalla B, Frohwein L, Buther F, Sch ¨ | afers K. Anthropomor- ¨
phic thorax phantom for cardio-respiratory motion simulation in tomographic imaging. Phys Med Biol. 2018;63:035009.
25. Chrysanthou-Baustert I, Polycarpou I, Demetriadou O, et al. Characterization of attenuation and respiratory motion artifacts and their influence on SPECT MP image evaluation using a dynamic phantom assembly with variable cardiac defects. J Nucl Cardiol. 2017;24:698–707.
26. Steidl P, Richter D, Schuy C, et al. A breathing thorax phantom with independently programmable 6D tumour motion for dosimetric measurements in radiation therapy. Phys Med Biol. 2012;57:2235–2250.
27. Kostiukhina N, Georg D, Rollet S, et al. Advanced Radiation DOSimetry phantom (ARDOS): a versatile breathing phantom for 4D radiation therapy and medical imaging. Phys Med Biol. 2017;62:8136–8153.
28. Perrin RL, Zakova M, Peroni M, et al. An anthropomorphic breathing phantom of the thorax for testing new motion mitigation techniques for pencil beam scanning proton therapy. Phys Med Biol. 2017;62:2486– 2504.
29. Perrin R, Peroni M, Bernatowicz K, et al. SU-D-BRE-01: a realistic breathing phantom of the thorax for testing new motion mitigation techniques with scanning proton therapy. Med Phys. 2014;41:111.
30. Colvill E, Krieger M, Bosshard P, et al. Anthropomorphic phantom for deformable lung and liver CT and MR imaging for radiotherapy. Phys Med Biol. 2020;65:07NT02.
31. Hubbell JH, Seltzer SM. X-Ray Mass Attenuation Coefficients. Radiation Physics Division, Physics Measurement Laboratory, National Institute of Standards and Technology. 2004. https://doi.org/10.18434/T4D01F.
32. Lindh WQ, Pooler M, Tamparo CD, Dahl BM. Delmar’s Comprehensive Medical Assisting: Administrative and Clinical Competencies. Boston: Cengage Learning; 2009. https://books.google.ca/books?id=AUhJKmKJ_eEC.
33. Bhatt DV, Mistry KN. Experimental study of friction under different variables on a piston-cylinder assembly. http://nacomm03.ammindia.org/Articles/Dyn009.pdf (http://nacomm03.ammindia.org/Articles/Dyn009.pdf)
34. Merrit D, Weinhaus F. The pressure curve for a rubber balloon. Am J Phys. 1978;46:976–977.
35. Larson K. Can you estimate modulus from durometer hardness for silicones? Published online 2019; https://www.dow.com/content/dam/dcc/documents/en-us/tech-art/11/11-37/11-3716-01-durometer-hardness-forsilicones.pdf?iframe=true. (https://www.dow.com/content/dam/dcc/documents/en-us/tech-art/11/11-37/11-3716-01-durometer-hardness-for-silicones.pdf?iframe=true)
36. Tolomatic. ERD Electric Cylinder Features and Options. https://www.tolomatic.com/products/product-details/erd-low-cost-electric-cylindersfor-pneumatic-cylinder-replacement/features-options. (https://www.tolomatic.com/products/product-details/erd-low-cost-electric-cylinders-for-pneumatic-cylinder-replacement/features-options)

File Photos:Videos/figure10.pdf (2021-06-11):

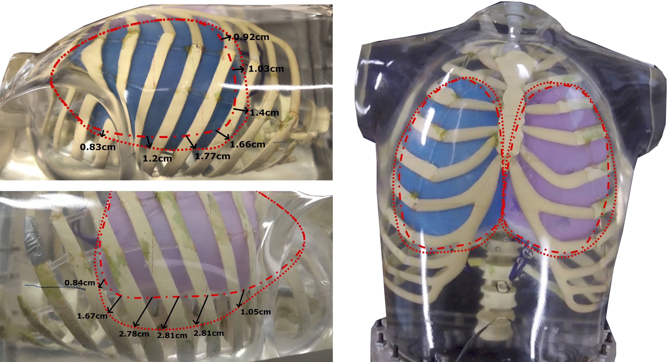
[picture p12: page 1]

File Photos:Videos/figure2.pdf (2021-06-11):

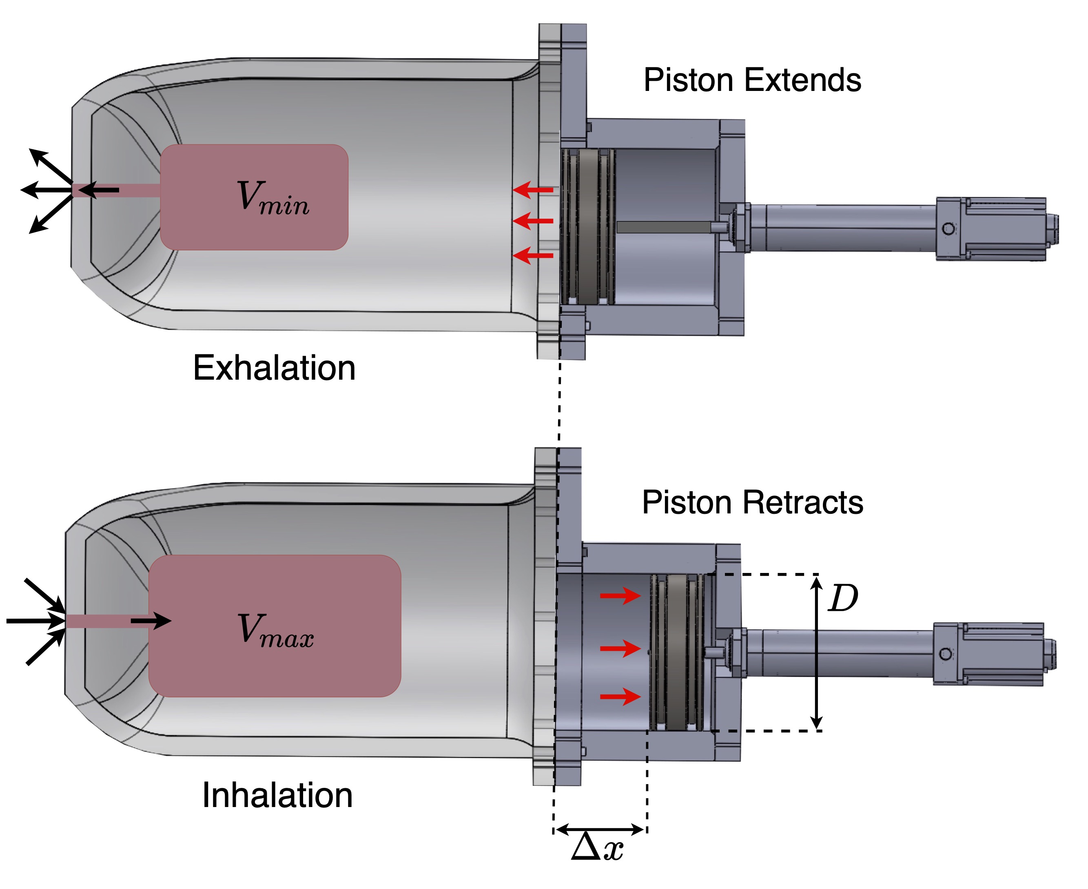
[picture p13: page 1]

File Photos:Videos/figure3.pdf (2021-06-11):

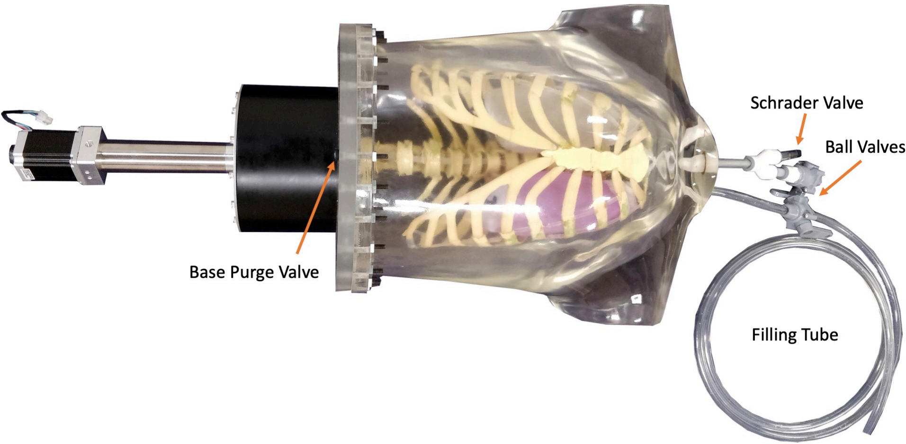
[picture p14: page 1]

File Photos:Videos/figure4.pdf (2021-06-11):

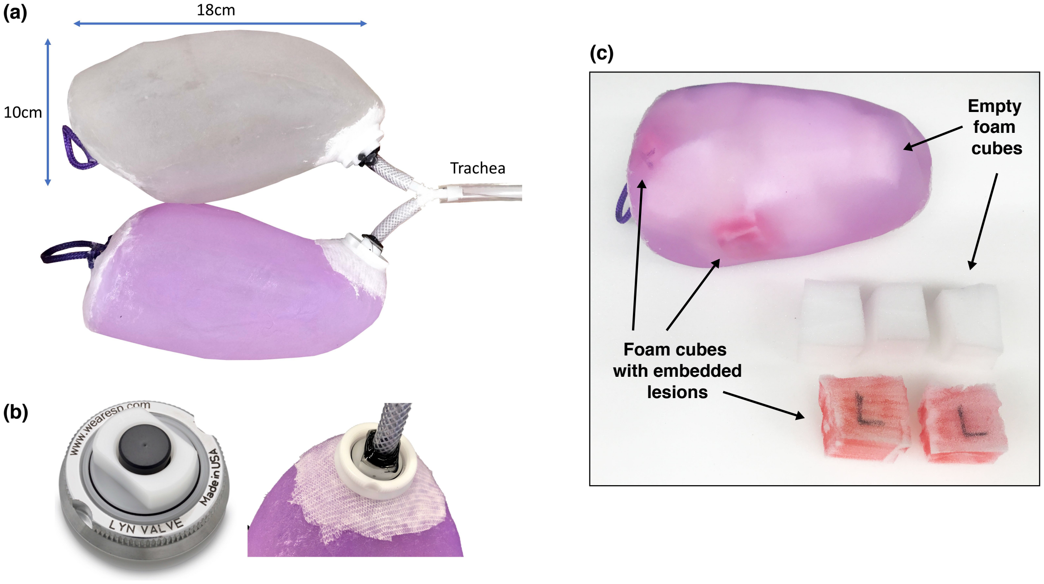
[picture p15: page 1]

(a)

(b)

(c)

Foam cubes
with embedded
lesions

Empty
foam
cubes

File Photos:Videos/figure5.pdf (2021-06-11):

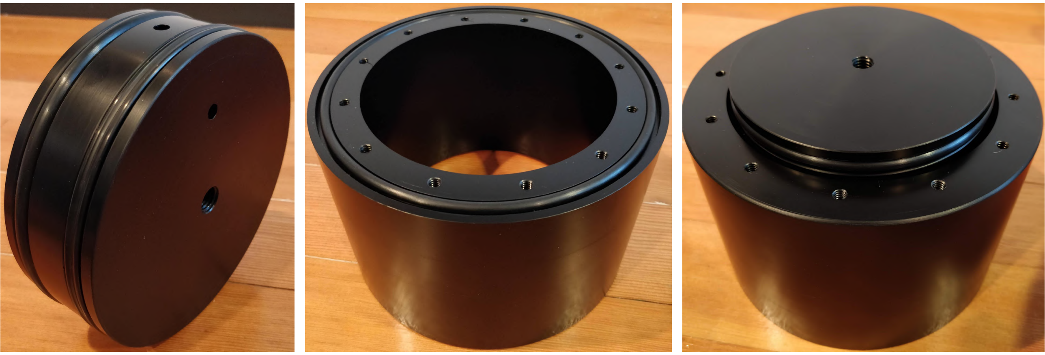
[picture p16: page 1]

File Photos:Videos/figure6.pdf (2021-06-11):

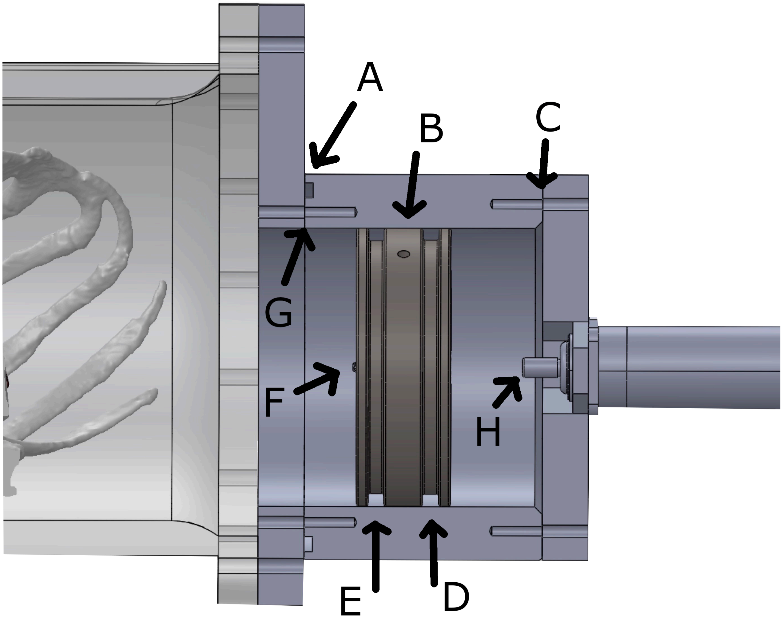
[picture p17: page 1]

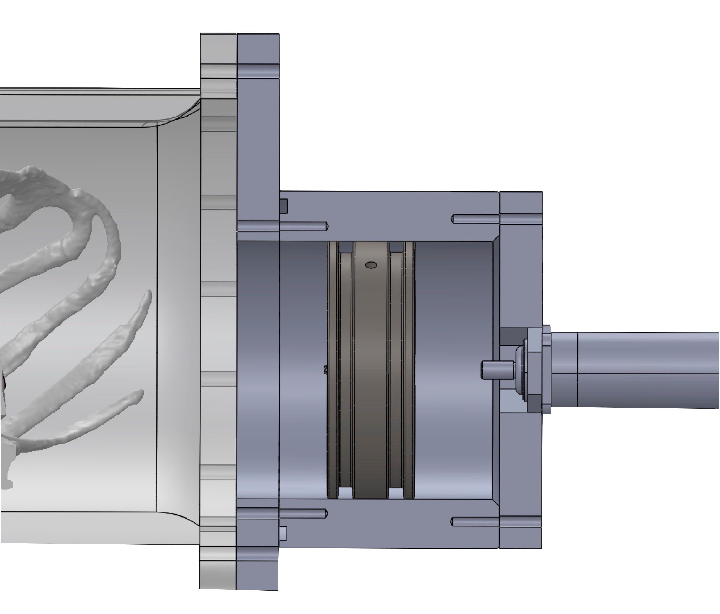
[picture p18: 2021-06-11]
Photos:Videos/pistonCloseup1.png

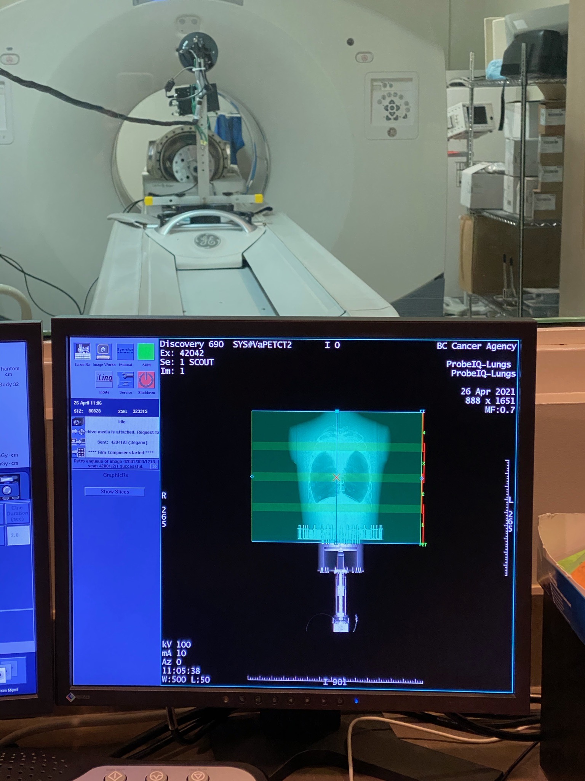
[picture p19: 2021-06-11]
Photos:Videos/3BDB1FC7-2954-4B7E-975D-0030990BF8111.jpg

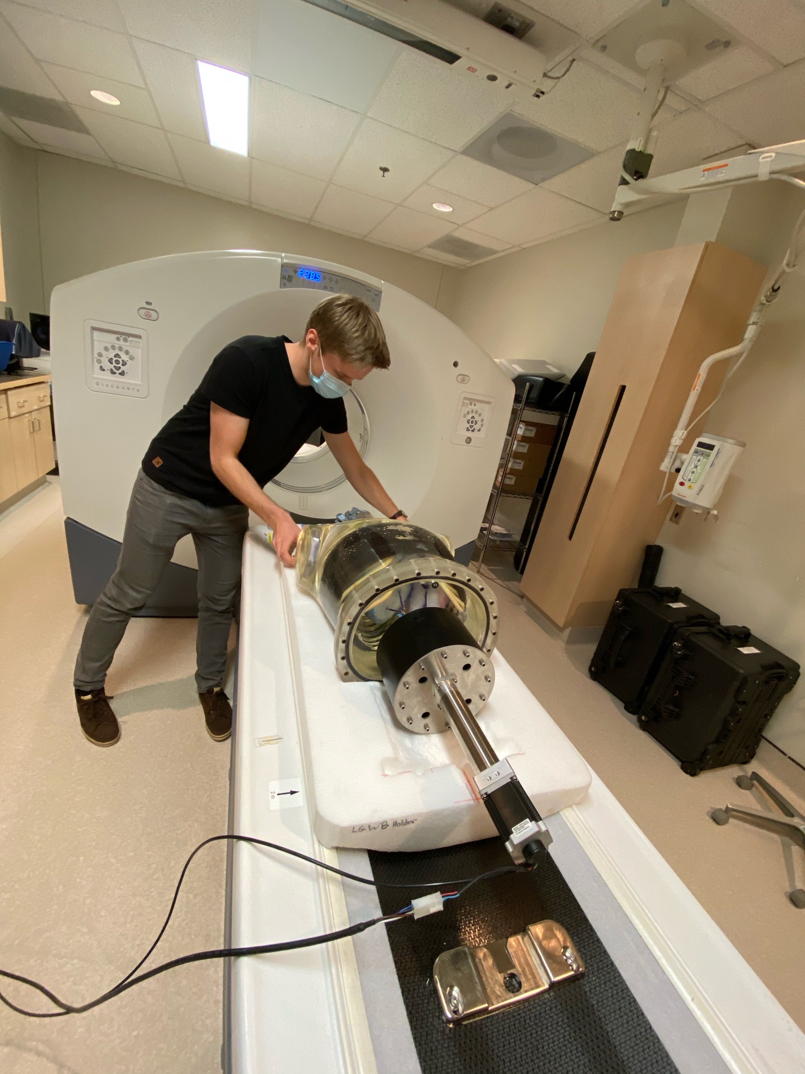
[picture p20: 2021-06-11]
Photos:Videos/9AF9EE87-D5B7-4244-9934-BE6E0896FF591.jpg

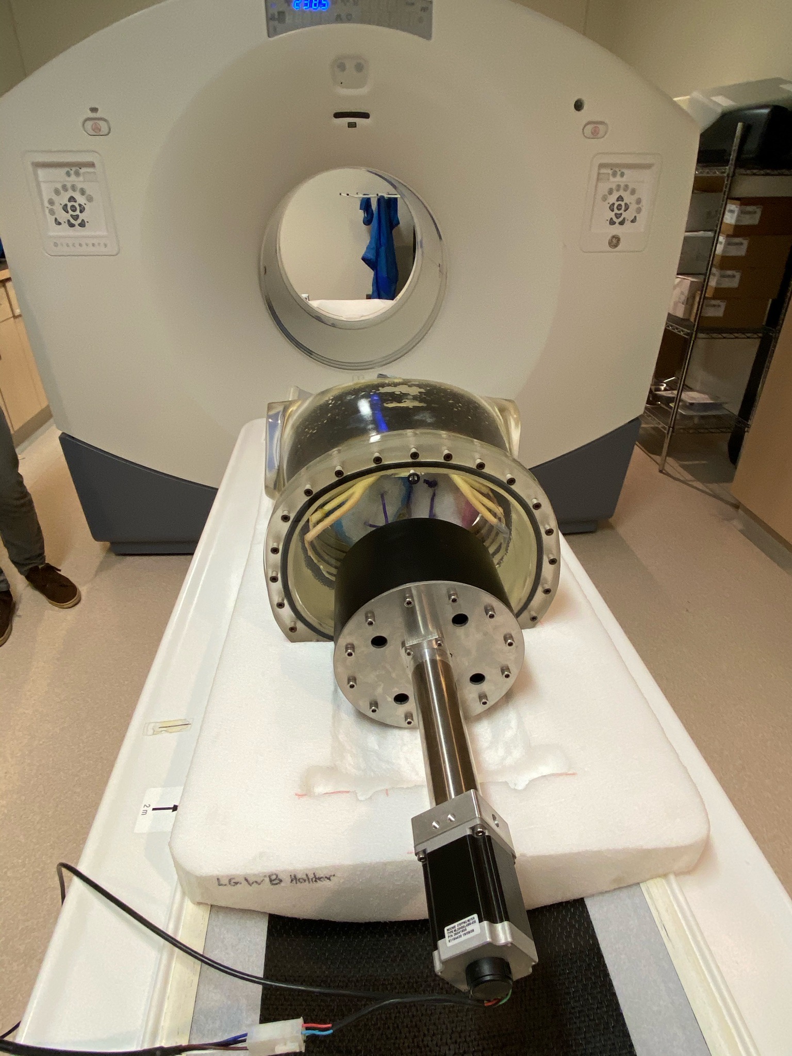
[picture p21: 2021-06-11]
Photos:Videos/7A2B42C9-8A91-4A77-BAF8-52FF9C687AEA.jpg

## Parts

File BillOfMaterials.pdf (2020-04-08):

Robot Phantom Bill of Materials

Creation Date: April 3 2020

Portion of Project | Part Number | Part Name | Manufacturer | Manufacturer Part Number | Supplier | Supplier Part Number | Quantity | Unit of Measurment | Procurement Type (OTS, MTO*) | Cost (CAD) | Associated Drawing | Datasheet | BOM Notes Lungs (L) | L-C35 | Chlorosil-35 | Ottobock Germany | 85P21=2 | Ottobock Germany | 85P21=2 | TBD | / (2kg container) | OTS | -$ | 302.40- | Purchased through of Desmond Cook, BCIT (Desmond_Cook@bcit.ca) L-Lun(R/L) | Lungs | In house- Barber Prosthetics | - | - | - | 1 | - | MTO | L-LunRL.SLDASM | Drawing is for lungs mold, 3D Printed PLA
L-TF(M/F)(R/L) | Lung-Trachea Fitting | In house | - | - | - | 2 | - | MTO | -$ | - - | L-TF.SLDASM (https://github.com/dgblack/robotPhantom/blob/master/CAD/L-TF.SLDASM) | 3D Printed PLA - One right (R), one left (L), each with a male (M) and female (F) part L-TFO(R/L) | Lung-Trachea Fitting O-ring | In house | - | - | - | 2 | - | MTO | -$ | - - | L-TFO.SLDPRT | Not yet spec'ed
Linear Acuator (LA) | LA-ERD15 | Tolomatic ERD15 Linear Actuator | Tolomatic | ERD15 BNM05 SM90.000 LMI ST1 FFG ARI | PQ Systems Ltd | ERD15 BNM05 SM90.000 LMI ST1 FFG ARI | 1 | each | OTS | -$ | 1,257.00- | LA-ERD15.SLDASM (https://github.com/dgblack/robotPhantom/blob/master/CAD/LA-ERD15.SLDASM) | ERD Brochure (https://www.tolomatic.com/Portals/0/Resources/becb99642abb4569a842619cb7afef64-orig.pdf?ver=2020-03-24-150427-307) | Contact Robert de Rot at PQ Systems for inquiries (robert@pqsystemsltd.com) LA-ACS | Tolomatic ACS Stepper Drive | Tolomatic | ACST1048UD | PQ Systems Ltd | ACST1048UD | 1 | each | OTS | -$ | 692.00- | - | ACS Driver Manual

LA-SM23

Tolomatic AMS NEMA23, 2-Stack Stepper Motor | Tolomatic | AMS1C2A1 | PQ Systems Ltd | AMS1C2A1 | 1 | each | OTS | -$ | 350.00- | LA-ERD15.SLDASM (https://github.com/dgblack/robotPhantom/blob/master/CAD/LA-ERD15.SLDASM) With 2000-count Encoder LA-SC3 | Tolomatic 3m Stepper Motor Cable | Tolomatic | CR33 | PQ Systems Ltd | CR33 | 1 | each | OTS | - | Came with actuator and stepper motor LA-EC3 | Tolomatic 3m Encoder Cable | Tolomatic | CR33 | PQ Systems Ltd | CR33 | 1 | each | OTS | - | Came with actuator and stepper motor LA-IC3 | Tolomatic 3m IO Cable | Tolomatic | CR33 | PQ Systems Ltd | CR33 | 1 | each | OTS | - | Came with actuator and stepper motor LA-PS48 | AC-DC Converter, 48 V 120 W | Mean Well USA Inc. | EDR-120-48 | Digikey Canada | 1866-1442-ND | 1 | each | OTS | -$ | 32.34- | - | EDR-120-48 Datasheet LA-WPC | Cord 18 AWG | Qualtek | 311007-01 | Digikey Canada | Q106-ND | 1 | each | OTS | -$ | 4.03- | - | Wall to Power Supply Cable (WPC) LA-PSC | Cord 18 AWG | Qualtek | 311007-01 | Digikey Canada | Q106-ND | 1 | each | OTS | -$ | 4.03- | - | Power Supply to Stepper-Driver Cable (PSC) LA-USB | USB Type A Male to Type B Male 30cm Cable | - | Project Lab | - | 1 | each | OTS | -$ | - - Actuation Mechanism (AM) | AM-PR429 | Oil Resistant Buna-N O-Ring, 1/4 Fractional Width | McMaster Carr | 9452K416 | McMaster Carr | 9452K416 | 1 | pack of 5 | OTS | -$ | 7.87- | - Dash Number 429
AM-CR364 | Oil Resistant Buna-N O-Ring, 3/16 Fractional Width | McMaster Carr | 9452K521 | McMaster Carr | 9452K521 | 1 | pack of 5 | OTS | -$ | 6.48- | - Dash Number 364
AM-PR353 | Oil Resistant Buna-N O-Ring, 3/16 Fractional Width | McMaster Carr | 9452K411 | McMaster Carr | 9452K411 | 1 | pack of 5 | OTS | -$ | 5.96- | - | To be tested for potential friction / water proofing improvements Dash Number 353
AM-PR429x | Oil Resistant Buna-N O-Ring, 1/4 Fractional Width | McMaster Carr | 90025K579 | McMaster Carr | 90025K579 | 1 | pack of 5 | OTS | -$ | 12.65- | - | To be tested for potential friction / water proofing improvements Dash Number 429, X-profile AM-P2O | Piston | UBC Physics and Astronomy Machine Shop | - | - | - | 1 | - | MTO | -$ | 442.77- | AM-P2O.SLDPRT | Cheaper labour cost as associated with UBC Physics and Astronomy Department AM-LPC | Lung to piston motion coupling cable mount | In house | - | - | - | 1 | each | MTO | -$ | - - | AM-LPC.SLDPRT | Not made yet - to be 3D printed or machined AM-Cyl | Cylinder | UBC Physics and Astronomy Machine Shop | - | - | - | 1 | - | MTO | -$ | 442.77- | AM-Cyl.SLDPRT | Cheaper labour cost as associated with UBC Physics and Astronomy Department Mounting (M) | M-1024-916
18-8 Stainless Steel Socket Head Screw | McMaster Carr McMaster Carr McMaster Carr McMaster Carr In house In house | 92196A243 92196A243 92196A243 92196A546 -- | McMaster Carr Project Lab Dan Kadrmas McMaster Carr -- | 92196A243 --92196A546 -- | 1 12 24 1 1 1 | pack of 50 each each pack of 25 each each | OTS OTS OTS OTS MTO MTO | -$ 5.82--$ - --$ - --$ -$ -$ 9.22- 1/4”-20 x 1-1/2” Fully Threaded M-BP - -- - | - 10-24 x 9/16” Fully Threaded M-1420-916 - 1/4"-20 x 9/16" Fully Threaded M-1420-214 - 1/4"-20 x 2-1/4" Partially Threaded M-1420-112 M-BP.SLDPRT M-MP.SLDPRT | Manufactured in PHAS Student Machine Shop M-MP Manufactured in PHAS Student Machine Shop

18-8 Stainless Steel Socket Head Screw

18-8 Stainless Steel Socket Head Screw

18-8 Stainless Steel Socket Head Screw Base Plate Mounting Plate

Control (C) | C-RPI4 | CanaKit Raspberry Pi 4 Starter Kit (4GB RAM) | CanaKit | PI4-4GB-STR32F-C4-BLK | Amazon Canada | B07WRMR2CX | 1 | each | OTS | -$ | 134.99- | - | Raspberry Pi Documentation (https://www.raspberrypi.org/documentation/) C-DAC | DAC | Adafruit Industries LLC | MCP4725 | Digikey Canada | 1528-1010-ND | 1 | each | OTS | -$ | 7.55- | - | MCP4725 Manual
Testing | Grade B7 Medium-Strength Steel Threaded Rod | McMaster Carr | 98750A473 | McMaster Carr | 98750A473 | 1 | each | OTS | -$ | 1.90- | - | Used for testing demo actuator 7/16”-20 Thread Size, 2” Long Grade B7 Medium-Strength Steel Threaded Rod | McMaster Carr | 93675A365 | McMaster Carr | 93675A365 | 1 | each | OTS | -$ | 4.33- | - | Used for testing demo actuator M12 x 1.75 mm Thread Size, 50 mm Long
Total Cost | -$ | 3,724.11-

*OTS: Off the Shelf MTO: Made to Order

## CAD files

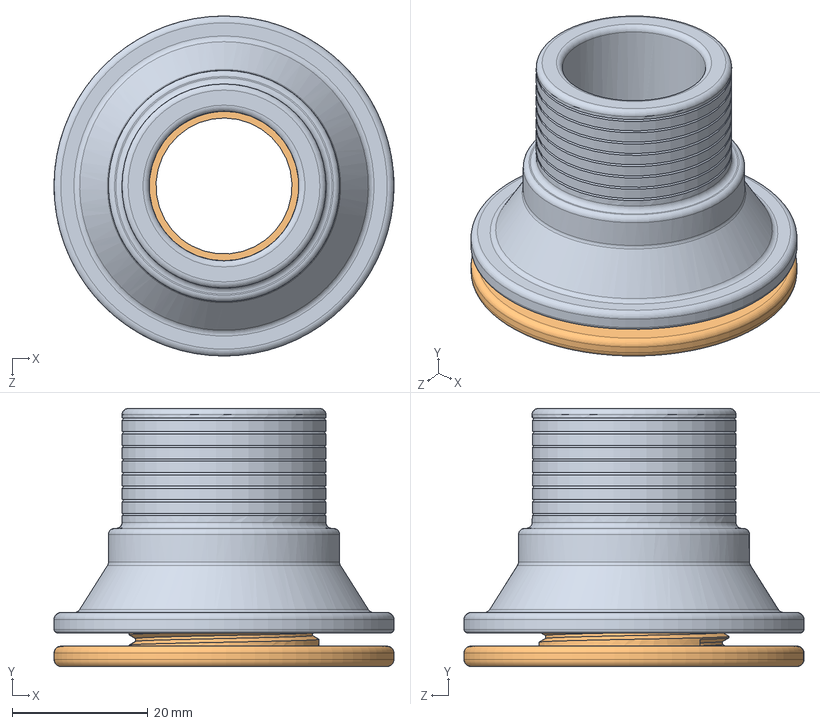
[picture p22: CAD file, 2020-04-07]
CAD/L-TF.SLDASM
50.0 x 37.9 x 50.0 mm
thruHullFitting_female
thruHullFitting_male
thruHullFitting_oring

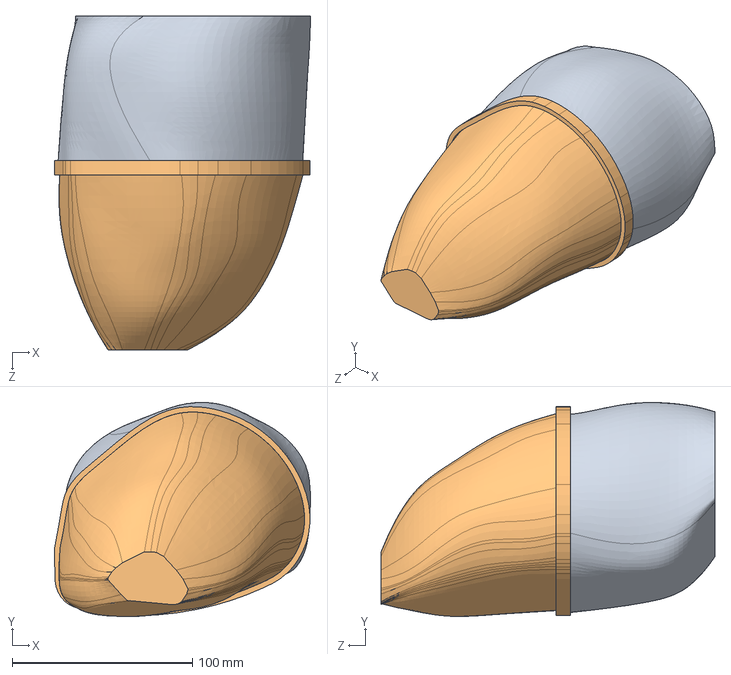
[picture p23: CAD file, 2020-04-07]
CAD/L-LunRL.SLDASM
142.0 x 118.6 x 185.1 mm
L-LunRL_lower
L-lunRL_upper

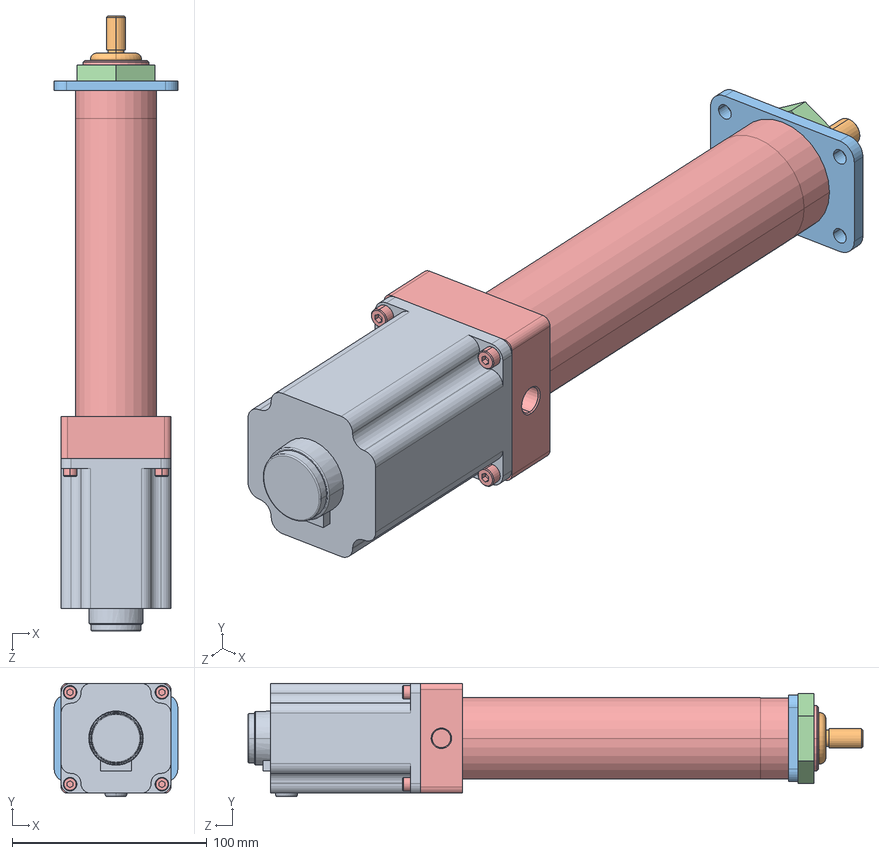
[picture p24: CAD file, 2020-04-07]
CAD/LA-ERD15.SLDASM
63.5 x 58.2 x 315.7 mm
36041955_ERD-321524-1.step
tempjoin3_21929307_ERD-321524-1.step
21921025_ERD-321524-1.step
21921020_ERD-321524-1.step
base_ERD-321524-1.step

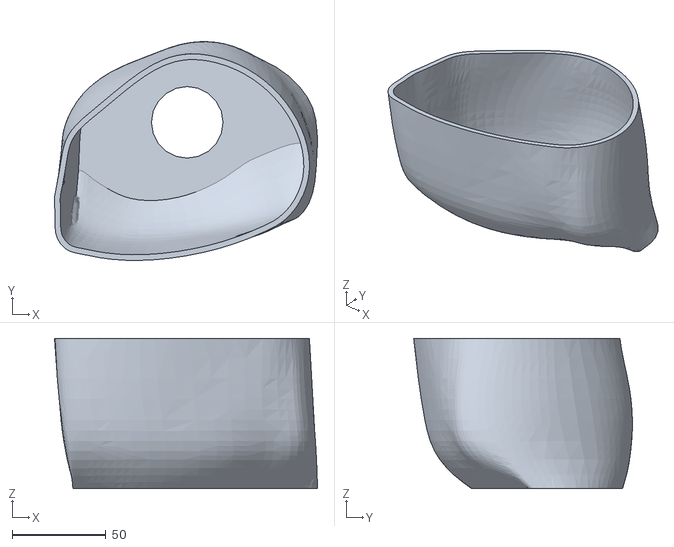
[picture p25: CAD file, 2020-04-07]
CAD/Fabrication/L-LunRL_lower.STL
139.9 x 116.4 x 80.0

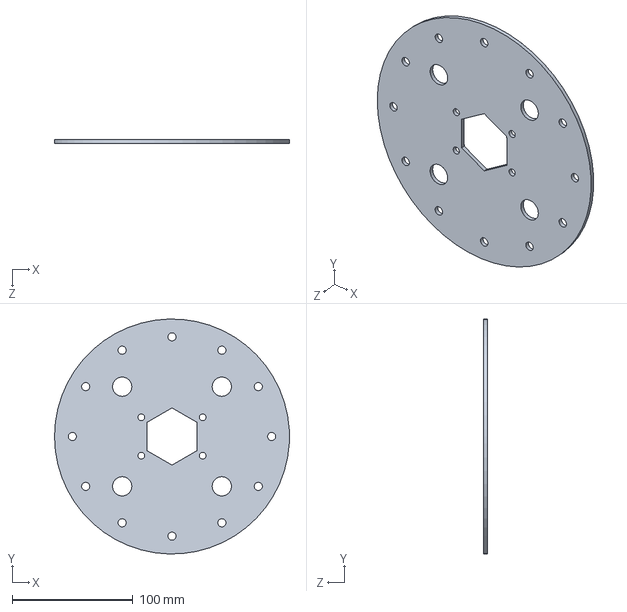
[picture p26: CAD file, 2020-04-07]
CAD/M-MP.SLDPRT
194.6 x 194.5 x 3.00 mm

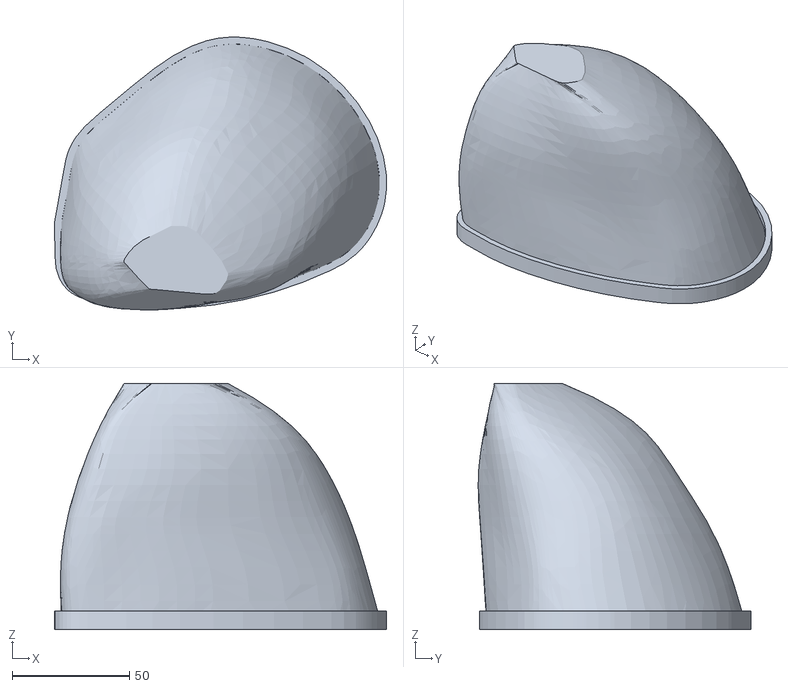
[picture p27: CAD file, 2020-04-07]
CAD/Fabrication/L-LunRL_upper.STL
141.6 x 116.3 x 105.0

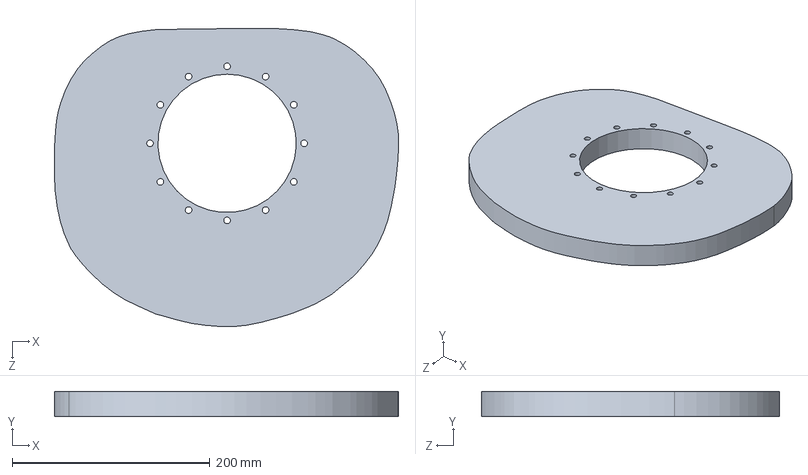
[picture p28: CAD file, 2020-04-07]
CAD/M-BP.SLDPRT
348.3 x 25.4 x 302.0 mm

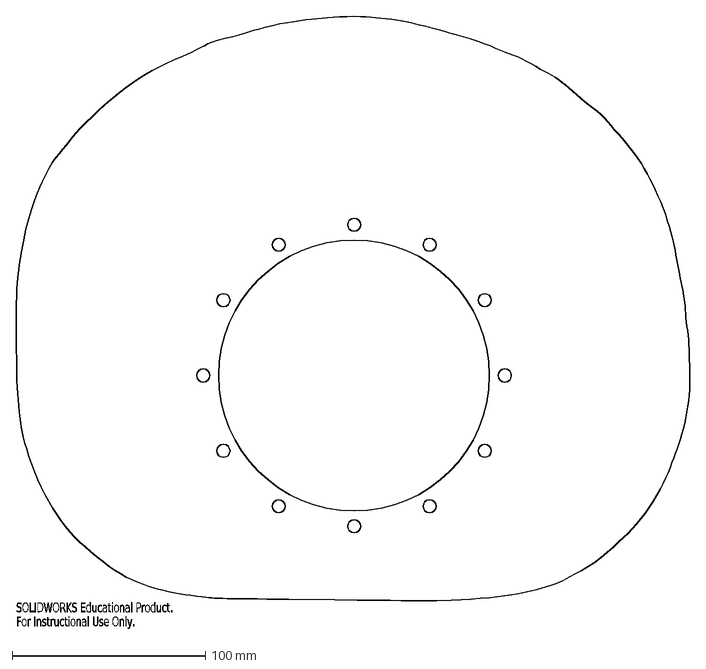
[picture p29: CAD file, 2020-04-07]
CAD/Fabrication/M-BP.DXF
SOLIDWORKS Educational Product.
For Instructional Use Only.

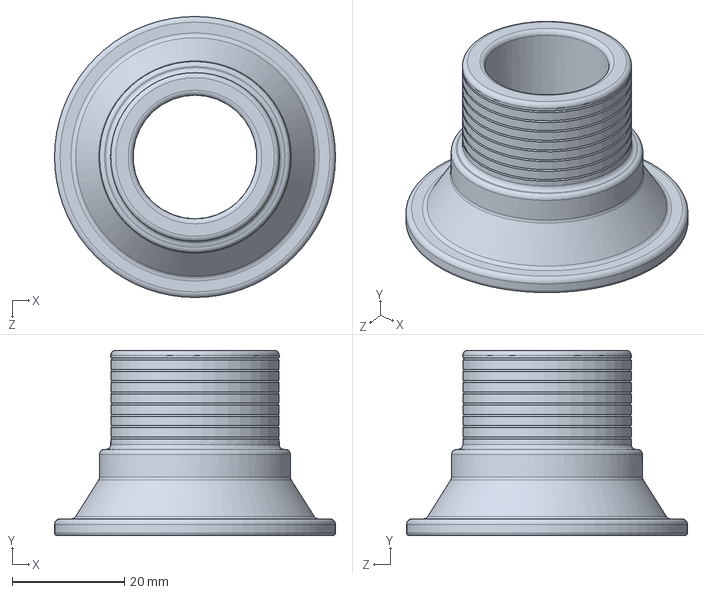
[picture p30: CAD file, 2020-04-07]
CAD/L-TFF.SLDPRT
50.0 x 33.0 x 50.0 mm

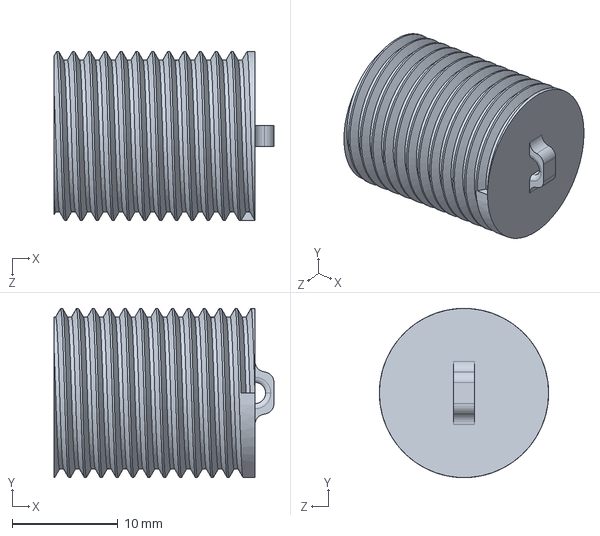
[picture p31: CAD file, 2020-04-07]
CAD/AM-LPC.SLDPRT
20.8 x 16.0 x 16.0 mm

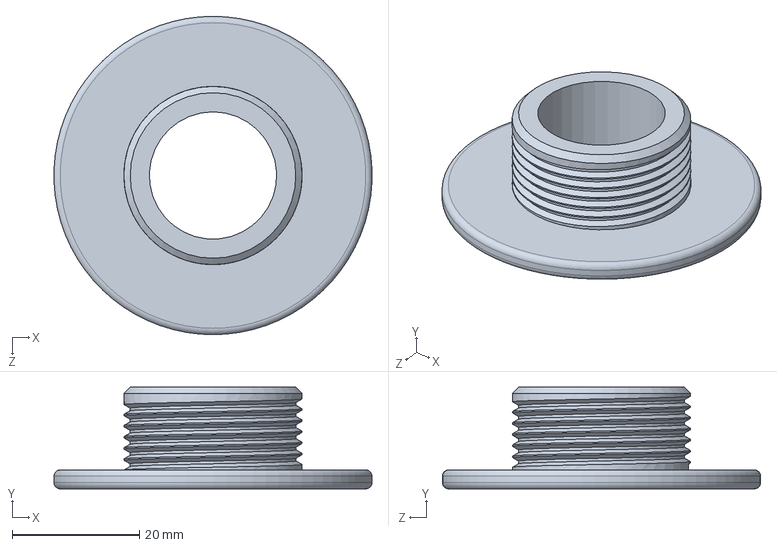
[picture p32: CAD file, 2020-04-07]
CAD/L-TFM.SLDPRT
50.0 x 16.0 x 50.0 mm

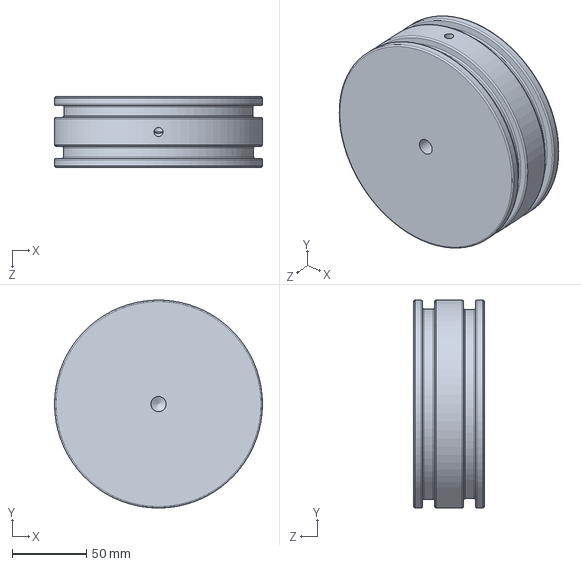
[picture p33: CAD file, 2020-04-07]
CAD/AM-P2O.SLDPRT
139.8 x 139.7 x 47.5 mm

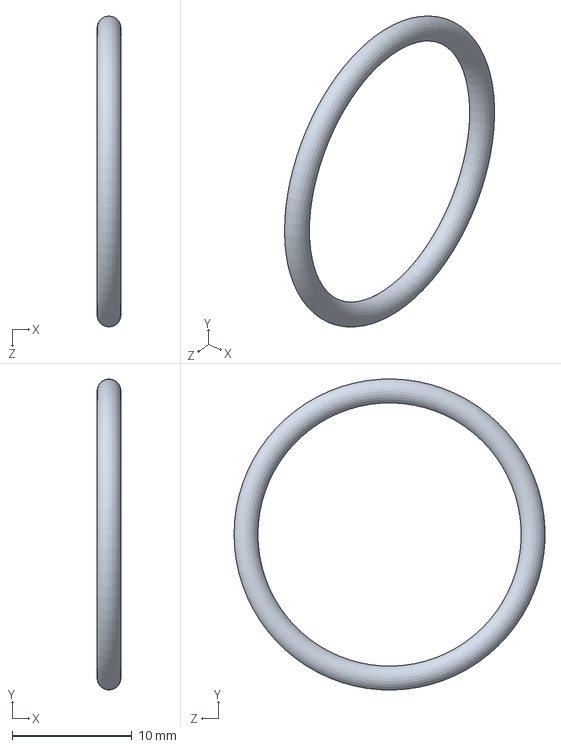
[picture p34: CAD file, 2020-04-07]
CAD/L-TFO.SLDPRT
2.00 x 26.0 x 26.0 mm

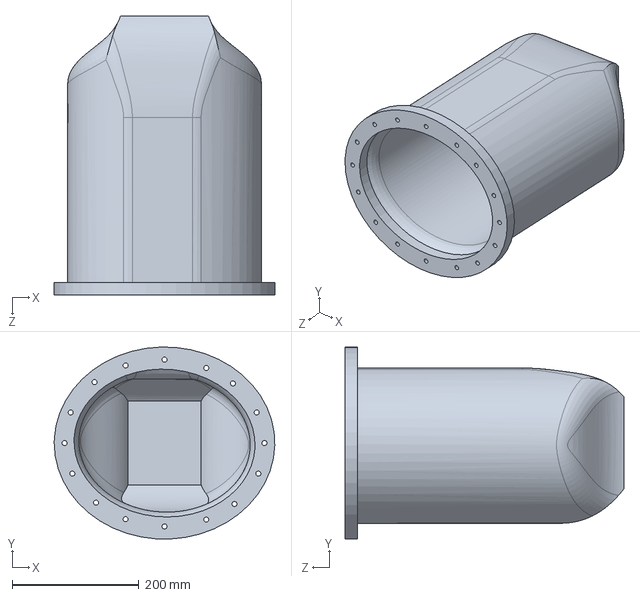
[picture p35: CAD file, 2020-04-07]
CAD/torso_DANN.SLDPRT
347.9 x 302.7 x 440.0 mm

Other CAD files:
CAD/L-LunRL_lower.SLDPRT
CAD/AM-Cyl.SLDPRT
CAD/L-lunRL_upper.SLDPRT
CAD/LeftLung.sldprt
CAD/Fabrication/AM-Cyl.SLDDRW
CAD/Fabrication/AM-P2O.SLDDRW

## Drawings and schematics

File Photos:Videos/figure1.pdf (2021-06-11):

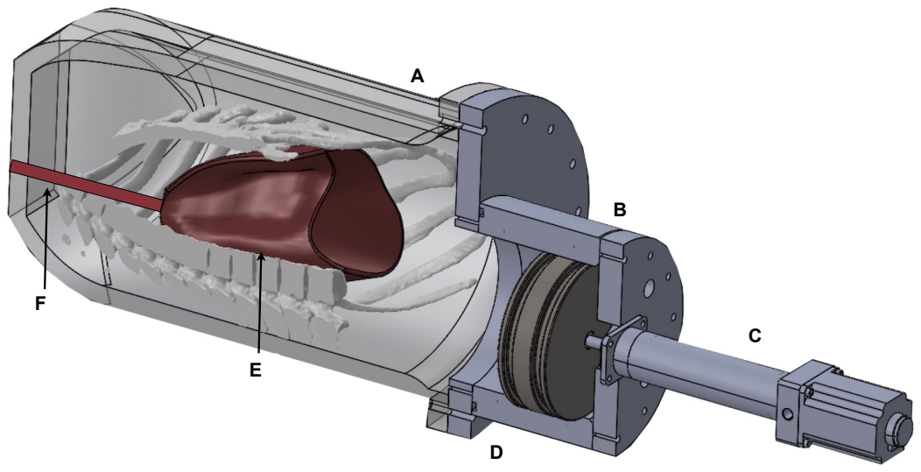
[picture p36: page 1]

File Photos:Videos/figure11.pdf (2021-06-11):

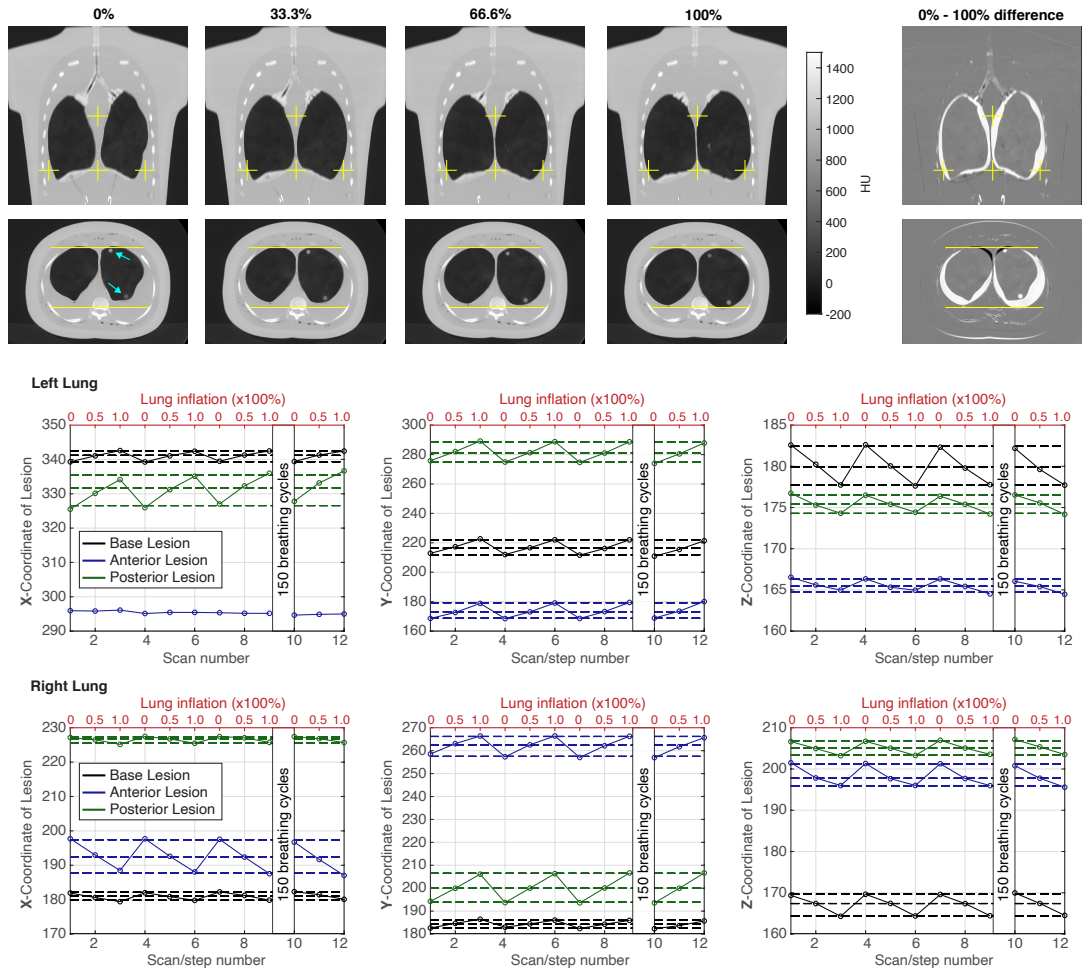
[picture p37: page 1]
Scan number; Lung inflation (x100%); Scan/step number; Left Lung; Right Lung; 150 breathing cycles; Lung inflation (x100%) 0.5 1.0 0 0.5 1.0 0 0.5 1.0 0 0.5; 0% - 100% difference

X-Coordinate of Lesion

Y-Coordinate of Lesion

Z-Coordinate of Lesion

Base Lesion Anterior Lesion
Posterior Lesion
